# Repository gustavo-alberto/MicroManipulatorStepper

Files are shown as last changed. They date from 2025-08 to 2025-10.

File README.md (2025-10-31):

# Open Micro Manipulator

This project contains an open source low-cost, easy-to-build motorized **XYZ Micro-Manipulator** motion control platform achieving submicron precision.
It's designed for applications such as optical alignment, probing electronic components, and microscopy.

Check out the YouTube video for more information about the device and how it is built:<br>
[An Open Source Motorized XYZ Micro-Manipulator - Affordable sub µm Motion Control](https://youtu.be/MgQbPdiuUTw)

<div style="display: flex; gap: 2%;">
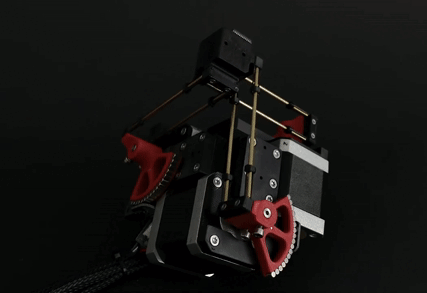
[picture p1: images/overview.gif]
  
  
</div>

Thanks to its parallel kinematic structure and miniature ball joints, it achieves good mechanical stiffness and a large range of motion.
The motors are off the shelf stepper motors driven by a 30 kHz closed loop controller and a very precise PWM signal.
A 'magnetic gearing' approach increases the resolution of the low-cost magnetic rotary encoders by a factor of 30 allowing for steps down to 50nm
(**Please mind the difference between resolution and accuracy**. The absolute accuracy is significantly worse.

The device can be controlled via simple G-Code commands over a USB serial interface and is thus easily integrated into other projects.
The firmware implements a complete motion planning stack with look-ahead for smooth and accurate path following capabilities.

## Getting Started

Below is a list of high level steps you can follow if you want to replicate the project. 
If you have questions or problems with the build or just want to discuss subjects related to the project, 
joint the projects community [Discord Server](https://discord.gg/maRvMVpa2Q).

1. Read this Document and watch the linked videos
2. Get the parts listed in [Bill of Materials](documentation/bom/bom.md)
3. Build the device and electronics
4. Change the hardware configuration according to your build [hw_config.h](firmware/MotionControllerRP/src/hw_config.h)
5. Upload firmware using VSCode with PlattformIO plugin
6. Calibrate axis

## 🐍 Python-API

The lightweight Python API handles all serial communication and provides convenient command execution and debug message printing.
The interface includes functions to home, move, and calibrate the device, as well as to query device information.
Simply copy the [open_micro_stage_api.py](software/PythonAPI/open_micro_stage_api.py) file into your project (also install the dependencies in requirements.txt), and you’re ready to get started.

## Usage Example
```python
from open_micro_stage_api import OpenMicroStageInterface

# create interface and connect
oms = OpenMicroStageInterface(show_communication=True, show_log_messages=True)
oms.connect('/dev/ttyACM0')

# run this once to calibrate joints
# for i in range(3): oms.calibrate_joint(i, save_result=True)

# home device
oms.home()

# move to several x,y,z positions [mm]
oms.move_to(0.0, 0.0, 0.0, f=10)
oms.move_to(3.1, 4.1, 5.9, f=26)
oms.move_to(0.0001, 0.0, 0.0, f=10)

# wait for moves to finish
oms.wait_for_stop()
```

## API Functions (most relevant functions only)
```python
connect(port, baud_rate=921600)
disconnect()
set_workspace_transform(transform)
get_workspace_transform()
home(axis_list=None)
calibrate_joint(joint_index, save_result)
move_to(x, y, z, f, move_immediately, blocking, timeout)
set_pose(x, y, z)
dwell(time_s, blocking, timeout)
enable_motors(enable)
wait_for_stop(polling_interval_ms, disable_callbacks)
set_max_acceleration(linear_accel, angular_accel)
set_servo_parameter(pos_kp, pos_ki, vel_kp, vel_ki, vel_filter_tc)
```

## ✨ Firmware v1.0.1

This update improves calibration, homing, logging, and adds several new G-Code commands.

### Improvements
- **Homing**: parallel homing support, higher repeatability, more accurate geometric reference  
- **Joint calibration**: refined procedure, persistent flash storage (no recalibration after reboot)  
- **Logging**: clearer and more detailed output  

### New G-Code Commands
- `G28` — Home joints (supports homing multiple axis simultanously for faster startup)
- `G24` — Set pose command (directly sets servo targets, bypassing motion controller)  
- `M17/M18` — Enable/Disable motors (with pose recovery from encoders on enable)  
- `M51` — Read encoder values  
- `M55` — Set servo loop parameters 
- `M56` — Joint calibration (with save-to-flash option)  
- `M57` — Read various information about the device state  
- `M58` — Read firmware version

## ⚙ CAD-Files

All CAD models are made in **FreeCAD** to allow everyone to view and modify the design without subscribing or paying for a proprietary CAD solution.
Note that most components are already designed with the goal to make them easily machinable on a 3-Axis CNC-Mill.
You can also 3D-Print the parts but have to live with thermal drift (carbon filled filaments can reduce this problem).

<div style="display: flex;">
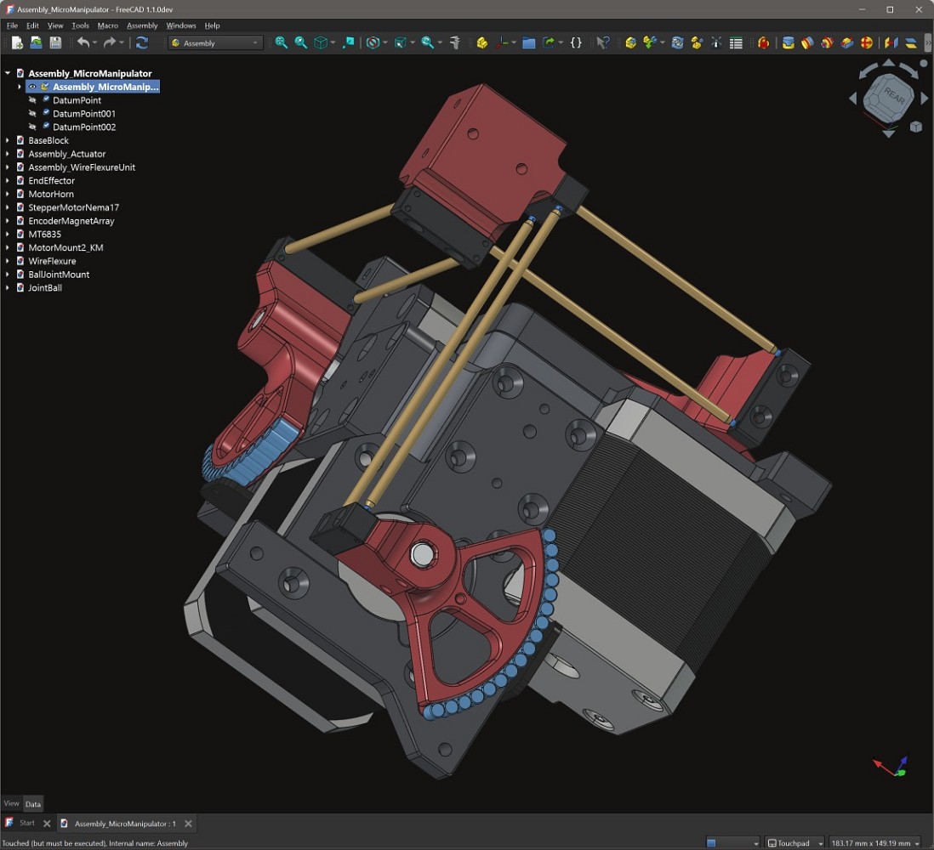
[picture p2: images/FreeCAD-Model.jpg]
FreeCAD Model
    
</div>

<br>

The CAD files can be found here: [CAD Models](construction).
Please note that FreeCAD version **1.1.0dev** was used, and the files might not work with older versions.

STL files for printing can be found here: [STL Files](construction/STL_3D_Printing/)

## ⚙ Kinematic Model

The kinematic model is defined here: [kinematic_model_delta3d.cpp](firmware/MotionControllerRP/src/kinemtaic_models/kinematic_model_delta3d.cpp).
Please check the dimensions of your build against the values set in the constructor. In particular, make sure the arm length matches.

## ⚙ Electronics

IMPORTANT: If you fabricated PCB version v1.2 (see version label on the board) you need to drill out a misplaced via on diode D1 that shorts 5V rail to ground (See [repair image](electronics/pcb_v1.2_fix.jpg) ). The problem was fixed in v1.3.

The electronics are designed in **KiCAD** and only commonly available modules (motor drivers and MCU boards) are used and connected by a simple PCB. No SMD soldering is required to populate the board to make the build extra accessible.
For usual winding resistance of your motors, the device should be powered by $${\color{lightgreen} 5V-6V }$$ (2A) to keep current and heating to a reasonable level.

<div style="display: flex; gap: 5%;">
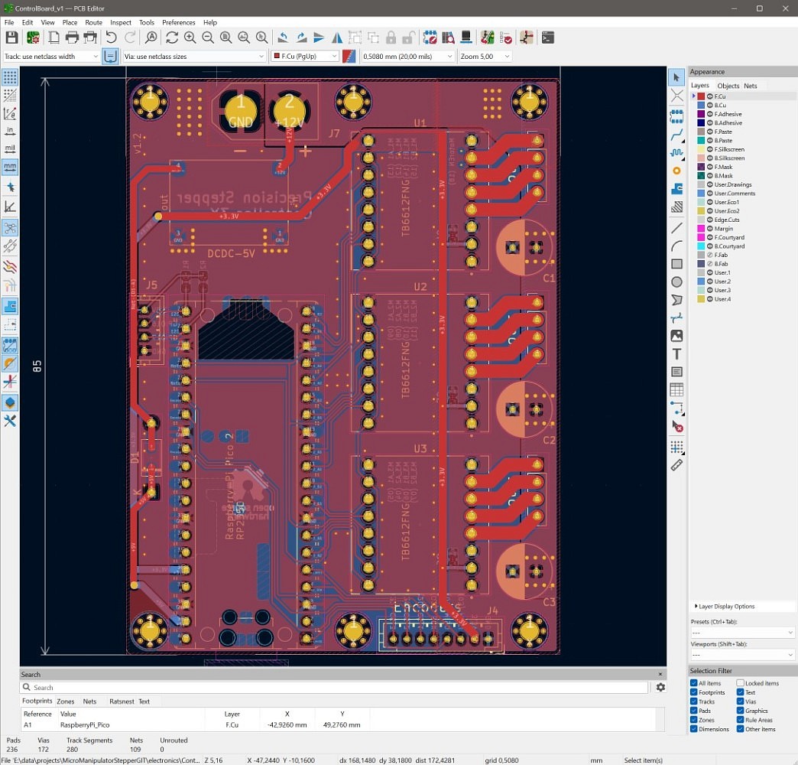
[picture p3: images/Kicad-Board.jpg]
  
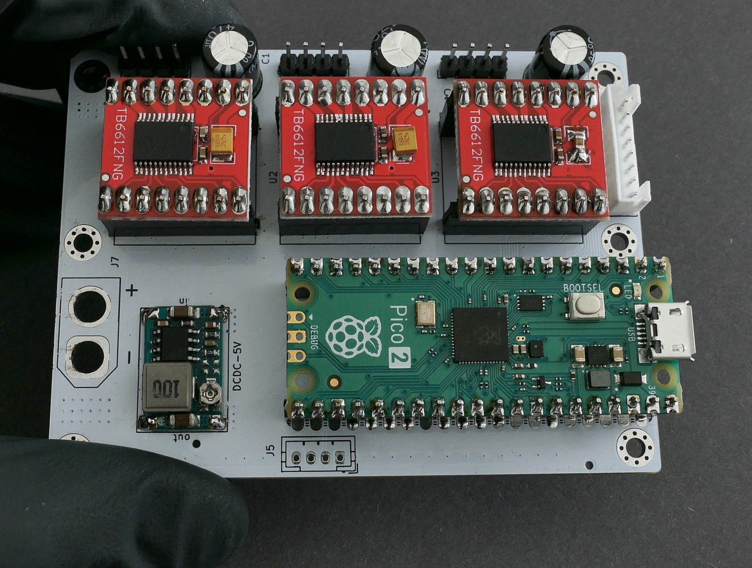
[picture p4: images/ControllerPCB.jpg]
  
</div>

## ⚙ Firmware

The firmware is written in C++ and takes some inspiration from the 'SimpleFOC' project. It aims to be streamlined and readable without any extra fuss, focusing on the hardware used in this project.
It implements path planning with look-ahead and, unlike many other motion controller projects, supports true 6DOF-Pose interpolation and planning, making it ready for driving hexapod motion platforms; that may or may not be the next step for this project.

You may find configuration for pin numbers, motor type, and other parameters in [hw_config.h](firmware/MotionControllerRP/src/hw_config.h). Please check them before uploading the firmware.

<div style="display: flex; gap: 2%;">
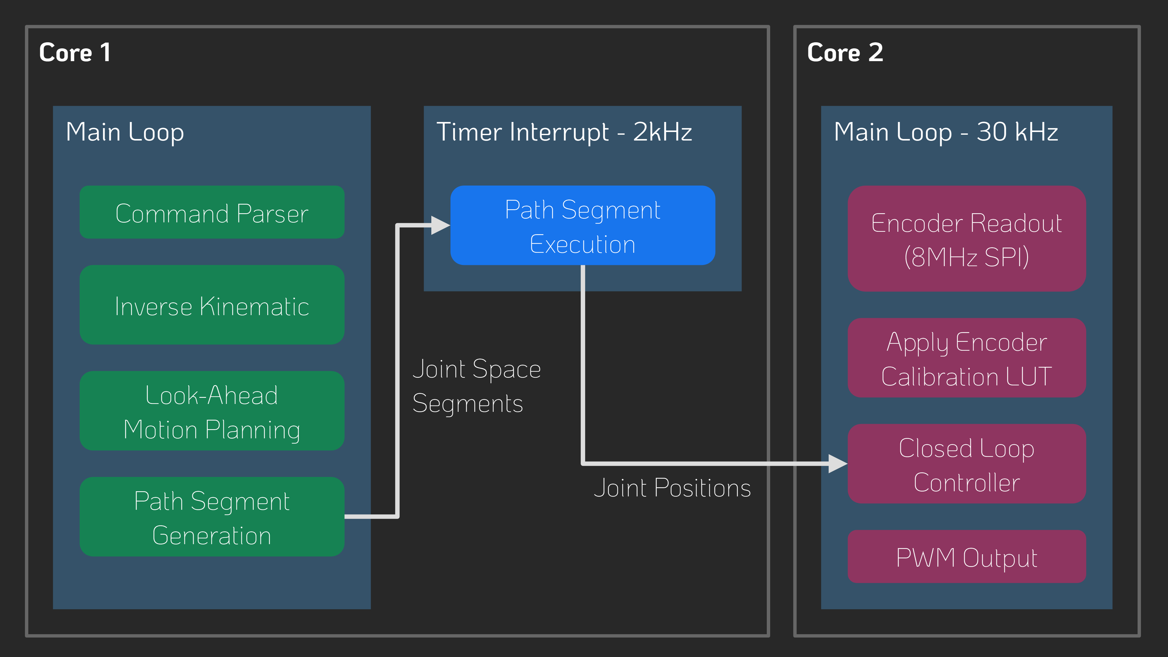
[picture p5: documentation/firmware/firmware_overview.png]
  
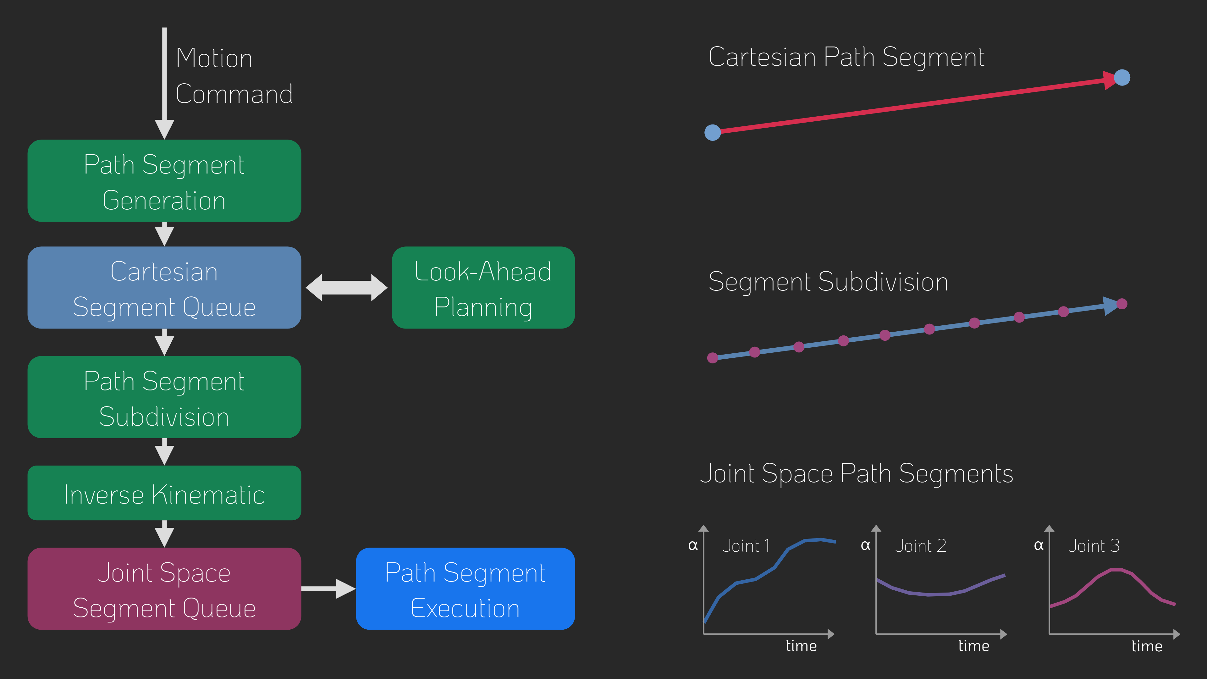
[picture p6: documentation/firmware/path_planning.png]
  
</div>

### Building and Flashing the Firmware

For building and flashing the firmware, Visual Studio Code (available for free on Windows and Linux) is recommended.
Install the PlatformIO add-on and open the firmware folder. You can now build and flash the firmware like any other PlatformIO project.

## ⚙ G-Code Interface

The firmware supports only a small subset of G-Code commands listed below.  
Each command is acknowledged with either an **`ok`** or **`error`** response.  

If a command provides additional information (e.g., the *get position* command), that information is returned **before** the `ok` message.  
The client must wait for an acknowledgment from the previous command before sending the next one—otherwise, behavior is undefined.
| Command           | Description                                                                 |
|-------------------|-----------------------------------------------------------------------------|
| `G0 X Y Z F`   | Move the end-effector in a straight line to the specified position. <br>• `X`, `Y`, `Z`: target positions <br>• `F`: feed rate |
| `G1 X Y Z F`   | Same as `G0`.                                                              |
| `G4 S/P`       | Dwell/pause for a specified time. <br>• `S`: seconds <br>• `P`: milliseconds |
| `G24 X Y Z A B C` | Directly set current pose for servo loops with optional rotation vector* `A`, `B`, `C`. |
| `G28 A-F`      | Home one or more joints. <br>• Optional joint selection `A`–`F`.           |
| `M17`          | Enable motors and read current pose as the start pose.                     |
| `M18`          | Disable motors.                                                            |
| `M50`          | Get current internal pose. (Encoders are not read here)                                   |
| `M51`          | Get current encoder angles (in degrees) and raw encoder values.              |
| `M52`          | Get the number of items in the planner queue.                               |
| `M53`          | Check if all planned moves are finished (`1` = finished, `0` = not finished). |
| `M55 A B C D F` | Set servo loop parameters. <br>• `A`, `B`: position PI controller gains (P and I) <br>• `C`, `D`: velocity PI controller gains (P and I) <br>• `F`: velocity filter time constant |
| `M56 J S`      | Calibrate a joint. <br>• `J`: joint index <br>• `S`: save calibration result |
| `M57`          | Get device and servo loop info: homing/calibration state, angles, loop frequencies, and file list. |
| `M58`          | Get firmware version.                                                      |
| `M204 L A`     | Set linear and angular acceleration. <br>• `L`: linear acceleration <br>• `A`: angular acceleration |

*Note: The communication protocol uses 3D vectors for rotations. The direction represents the rotation axis and the length of the vector represents the angle of rotation around the axis.

## ❤️ Support

If you'd like to support this project, consider the following:

- **Contribute to the build guide** – Help improve or expand the build instructions by submitting pull requests or opening issues with suggestions.
- **Characterize typical radial stepper motor shaft error motion** – Measure radial error motion of the shaft of multiple Nema-17 stepper motors (see Cylos Garage for more information about the subject: https://www.youtube.com/watch?v=gt2gK-oxy5s).
- **Give feedback on the build experience** – Let us know what worked, what didn’t, and how the process could be smoother for others.
- **Support the project on Ko-fi** – If you find this project valuable, you can support it financially via [Ko-fi](https://ko-fi.com/diffractionlimited) ☕.

## Youtube Video
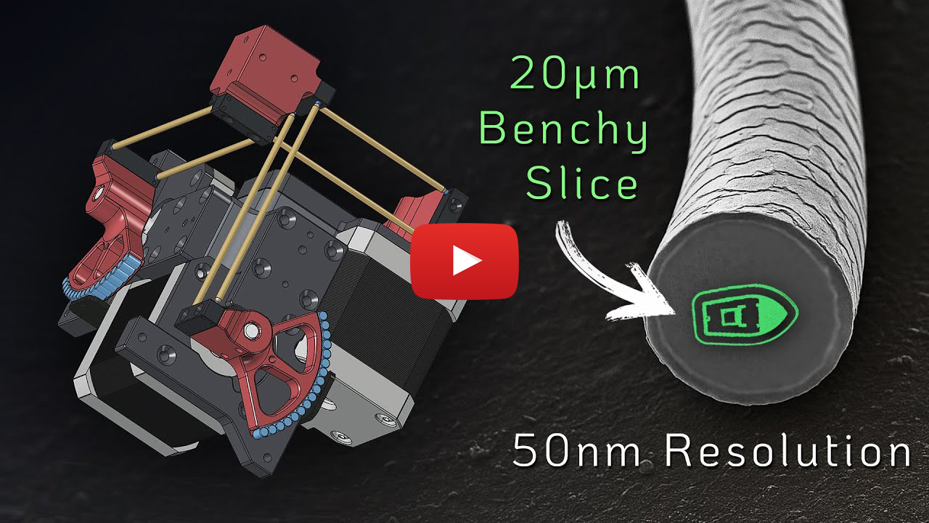
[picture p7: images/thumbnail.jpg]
Watch the video (https://youtu.be/MgQbPdiuUTw)


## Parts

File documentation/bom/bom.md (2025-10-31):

# Bill of Materials (BOM)

## Mechanics
| Name | Qty | Description | Comments | Suggested link | Image |
|------|-----|-------------|----------|----------------|-------|
| Steel ball | 12 | Ø1.25 mm (0.05") | Precision G10 or better. Can be sourced from small ball bearings | |
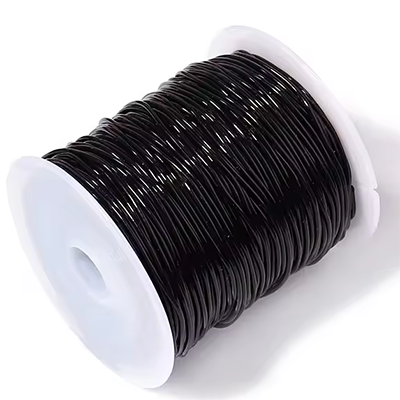
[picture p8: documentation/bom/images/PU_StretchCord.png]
Pu strech cord
| PU stretch cord | 1 m | Ø1mm | e.g. "Stretch Magic" or "Magic String" | [Aliexpress](https://www.aliexpress.us/item/3256805953910514.html)| |
| Neodym Cylinder Magnet | 70 | Ø3mm h=4 mm | N42 Grade | [Ebay Link](https://www.ebay.de/itm/365333642187?var=635110190027)|
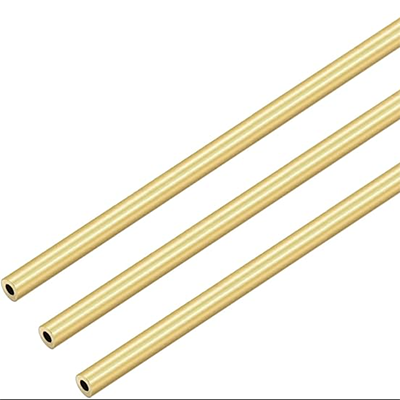
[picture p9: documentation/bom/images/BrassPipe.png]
Brass Pipe
| Brass Pipe | 1 m | OD=Ø2mm ID=Ø1 mm |  | [Amazon](https://a.co/d/1pRFmtf)| |
| M2 Screw | 12 | M2×12 mm, Countersunk |  | |
| M3 Grub Screw | 6 | M3×4 |  | |

## Electronics
| Name | Qty | Description | Comments | Suggested link | Image |
|------|-----|-------------|----------|----------------|-------|
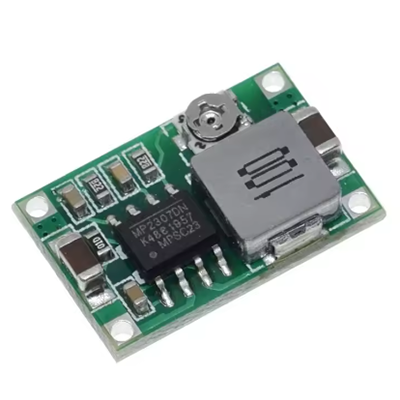
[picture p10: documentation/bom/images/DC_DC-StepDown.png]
DC-DC Step Down
| DC-DC Step Down Module | 1 | 4.75–23 V Step-Down Buck Converter |  | [Aliexpress](https://www.aliexpress.us/item/3256806752772875.html)| |
| (1N5819) OR (PMEG4010) | 1 | Diode (through-hole or SMD) |  | |
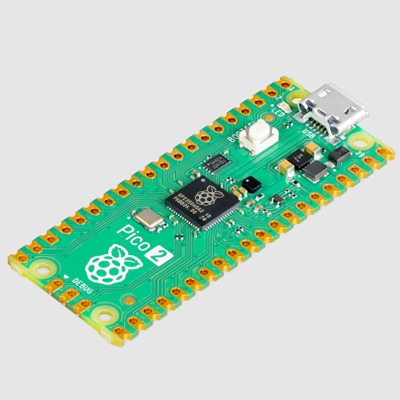
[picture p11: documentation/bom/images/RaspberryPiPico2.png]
Raspberry Pi Pico 2
| Raspberry Pi Pico 2 | 1 | Microcontroller board |  | | |
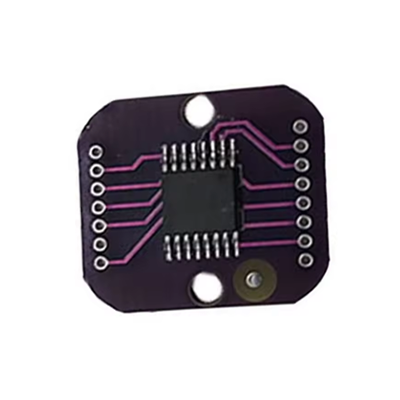
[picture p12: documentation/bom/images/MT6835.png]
MT6835 Magnetic Encoder Module
| MT6835 Magnetic Encoder Module | 3 | Magnetic encoder |  | [Aliexpress](https://www.aliexpress.us/item/3256808005140674.html)| |
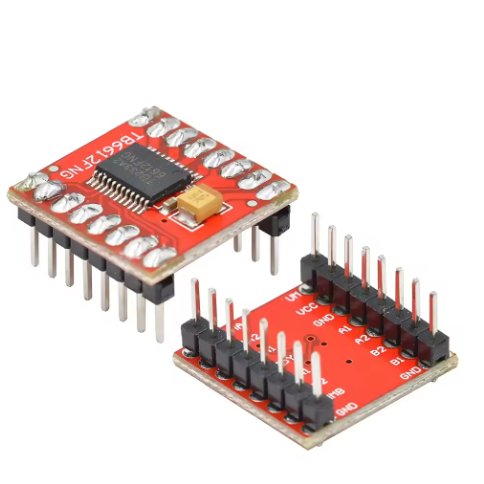
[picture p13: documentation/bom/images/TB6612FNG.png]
TB6612FNG Driver
| TB6612FNG Driver | 3 | |  | [Aliexpress](https://www.aliexpress.us/item/3256806060073976.html)| |
| 470 µF Electrolytic Capacitor | 3 | > 100 µF | anything > 100µF will work well | |
| 10 µF Ceramic Capacitor 0603 | 3 | Optional |  | |
| 4.7 k Resistor 0603 | 2 | Optional |  | |
| 2 Pin Power Header | 1 | 7.5 mm pitch |  | |
| 4 Pin Header | 4 | 2.5 mm pitch |  | |
| 8 Pin Header | 1 | 2.0 mm pitch |  | |
| NEMA 17 Stepper Motor | 3 | Body ≤ 38 mm | Body length <= 38mm | |

## 3D Printing
| Name | Qty | Description | Comments | Image |
|------|-----|-------------|----------|-------|
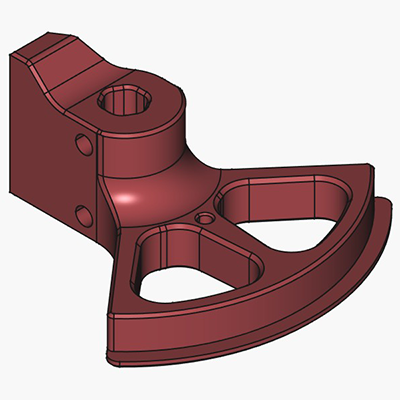
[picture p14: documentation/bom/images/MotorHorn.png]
Motor Horn
| Motor Horn | 3 |  | 0.4 mm+ nozzle may require post-processing | |
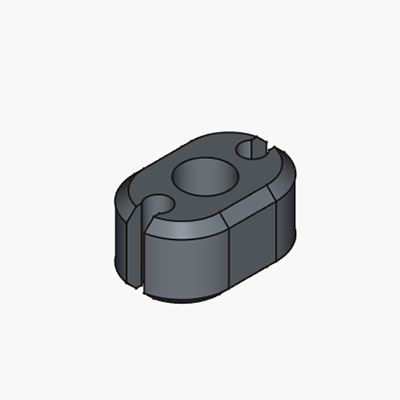
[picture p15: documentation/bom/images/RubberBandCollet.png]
Rubber Band Collet
| RubberBandCollet | 12 |  | 0.4 mm nozzle, 0.1mm Layer height + may require post-processing | |
| BallJointMount | 6 |  | 0.4 mm nozzle, 0.1mm Layer height + may require post-processing | Ball Joint Mount|
| Motor Mount | 3 |  |  | Motor Mount|
| End Effector | 1 |  |  | End Effector|
| Base Block | 1 |  |  | Base Block|

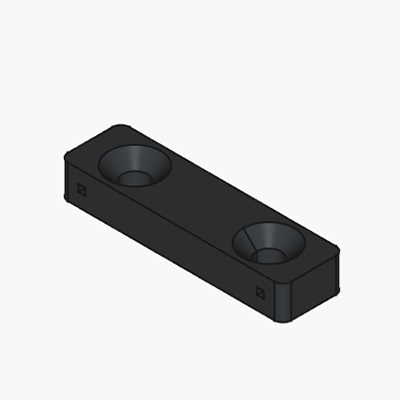
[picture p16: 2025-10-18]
documentation/bom/images/WireFlexureMount.png

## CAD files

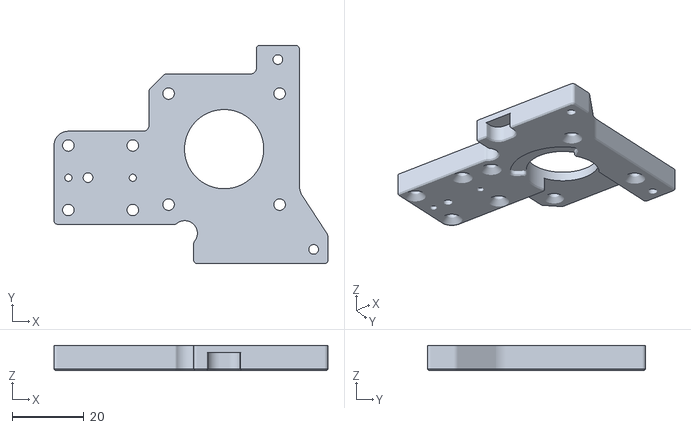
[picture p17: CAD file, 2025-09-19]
construction/v3_3dprinting_stl/MotorMount.stl
76.5 x 61.0 x 7.00

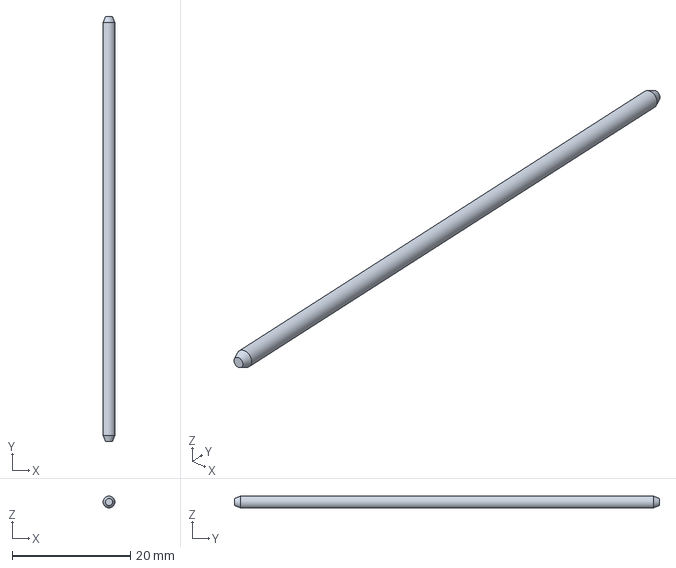
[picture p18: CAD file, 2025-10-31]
construction/v3/WireFlexure.FCStd
2.00 x 72.0 x 2.00 mm

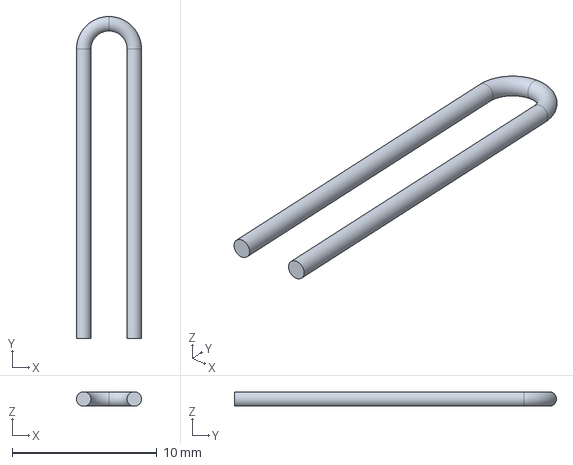
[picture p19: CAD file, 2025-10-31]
construction/v3/RubberBand.FCStd
4.50 x 22.2 x 1 mm

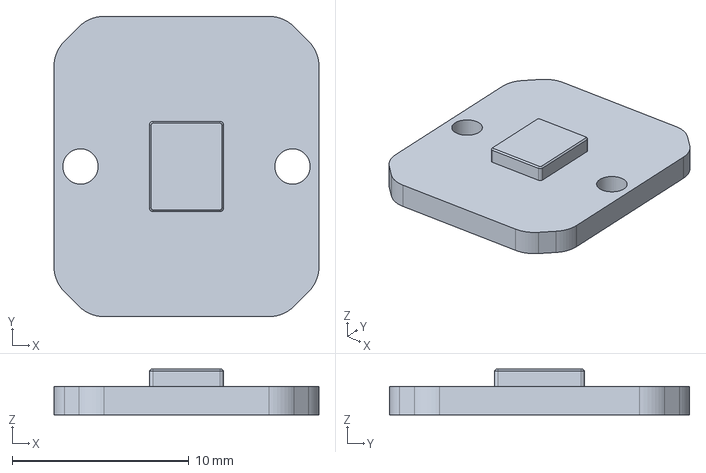
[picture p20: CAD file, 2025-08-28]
construction/v3/MT6835.FCStd
15.0 x 17.0 x 2.60 mm

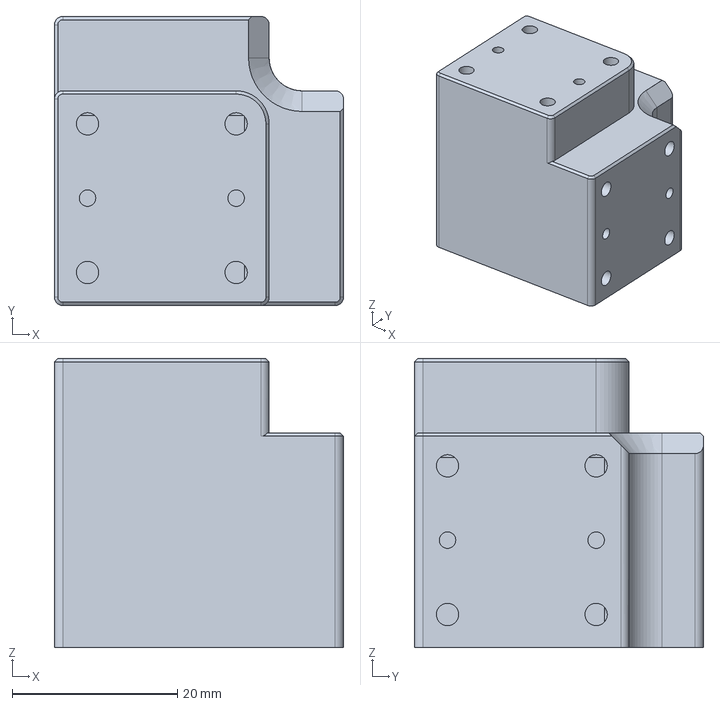
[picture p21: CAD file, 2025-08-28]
construction/v3/BaseBlock.FCStd
35.0 x 35.0 x 35.0 mm

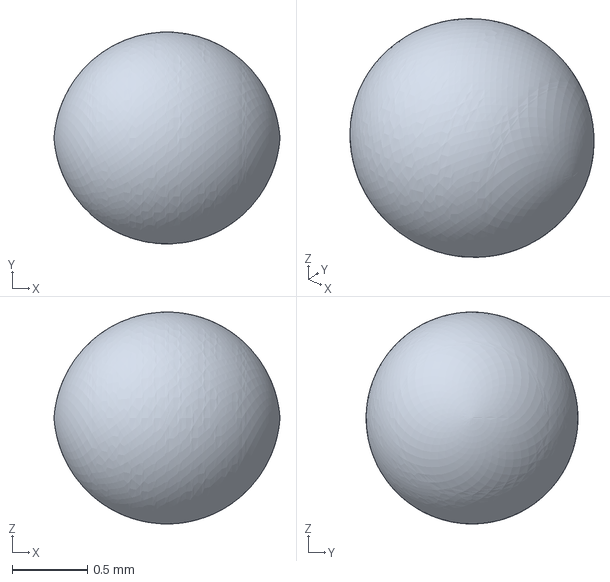
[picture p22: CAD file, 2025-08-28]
construction/v3/JointBall.FCStd
1.50 x 1.40 x 1.40 mm

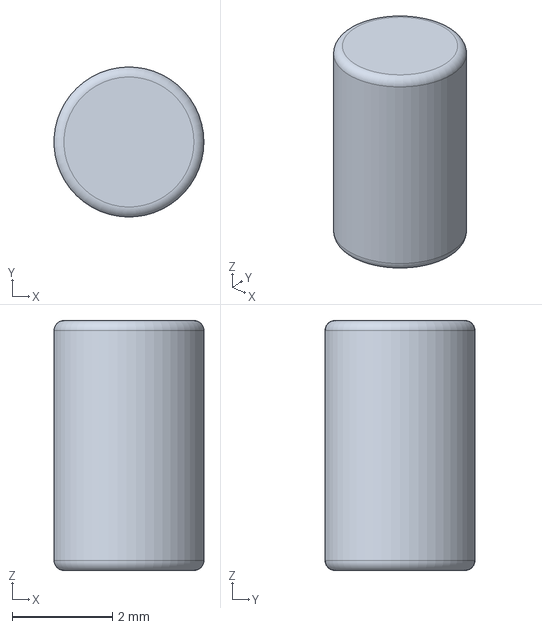
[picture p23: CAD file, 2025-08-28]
construction/v3/EncoderMagnet.FCStd
3.00 x 3.00 x 5.00 mm

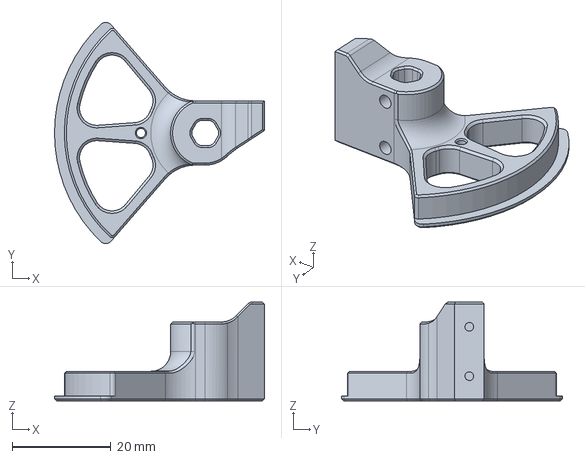
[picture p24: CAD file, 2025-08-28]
construction/v3/MotorHorn.FCStd
42.5 x 44.7 x 20.0 mm

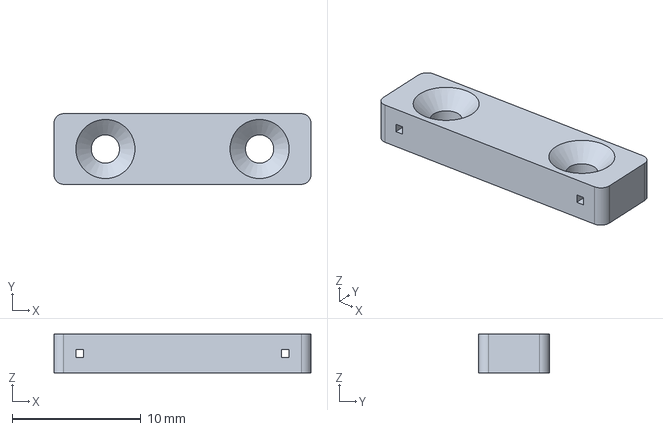
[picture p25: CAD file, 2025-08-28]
construction/v3/WireFlexureMount.FCStd
20.0 x 5.50 x 3.00 mm

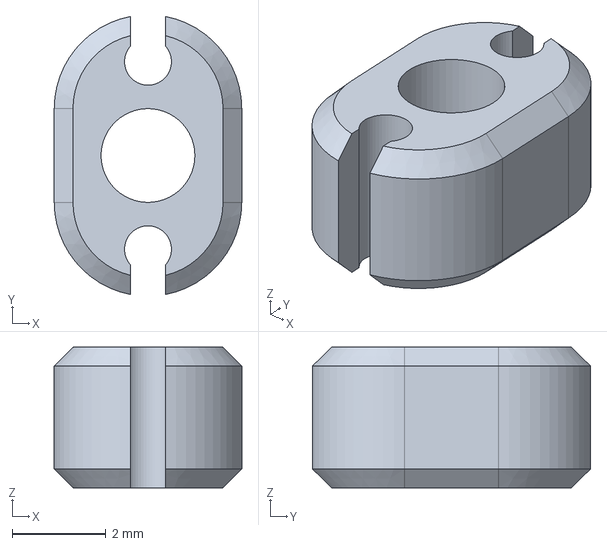
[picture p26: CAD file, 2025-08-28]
construction/v3/RubberBandCollet.FCStd
4.00 x 5.93 x 3.00 mm

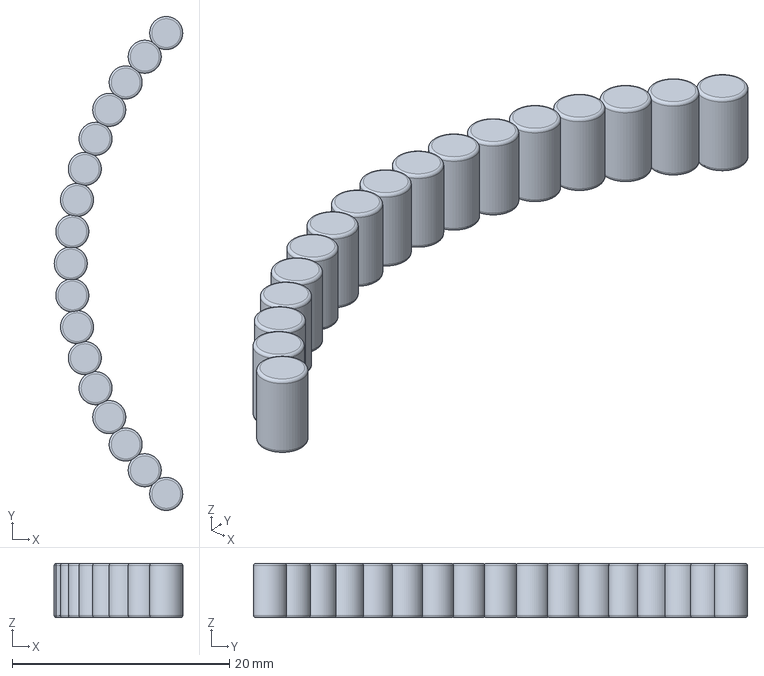
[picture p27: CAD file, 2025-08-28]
construction/v3/EncoderMagnetArray.FCStd
11.8 x 45.5 x 5.00 mm

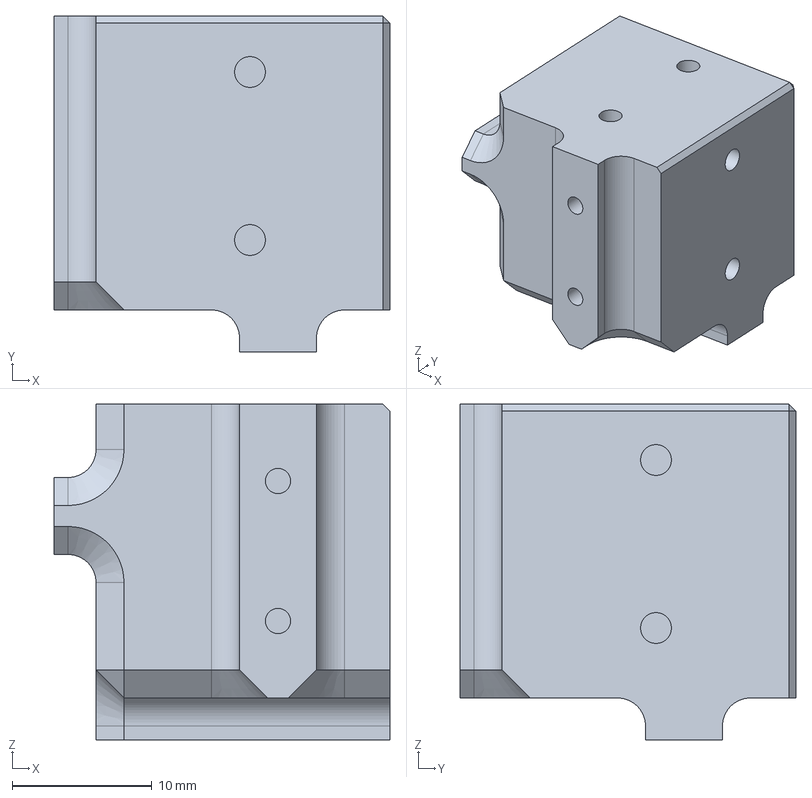
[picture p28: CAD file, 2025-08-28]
construction/v3/EndEffector.FCStd
24.0 x 24.0 x 24.0 mm

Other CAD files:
construction/v3/Assembly_MicroManipulator.FCStd
construction/v3/Assembly_Actuator.FCStd
construction/v3/Assembly_WireFlexureUnit.FCStd
construction/v3/Assembly_MicroManipulator_backup.FCStd
construction/v3/Assembly_EndEffector.FCStd
construction/v3/MotorMount2_KM.FCStd
construction/v3/BallJointMount.FCStd
construction/v3/StepperMotorNema17.FCStd
construction/v3_3dprinting_stl/BallJointMount.stl
construction/v3_3dprinting_stl/BaseBlock.stl
construction/v3_3dprinting_stl/EndEffector.stl
construction/v3_3dprinting_stl/MotorHorn.stl
construction/v3_3dprinting_stl/RubberBandCollet.stl
construction/v3_3dprinting_stl/WireFlexureMount.stl

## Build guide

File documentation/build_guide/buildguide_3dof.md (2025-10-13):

# Open MircoManipulator 3DOF - Build Guide

This document shall provide an easy to follow build guide and help with material selection like glues/magnets and so on.
The following structure is just a placeholder, feel free to contribute...

## Introduction

## Bill of Materials

## Components
### Mechanical Parts
### Magnet Selection

## Balljoints
## Assembly

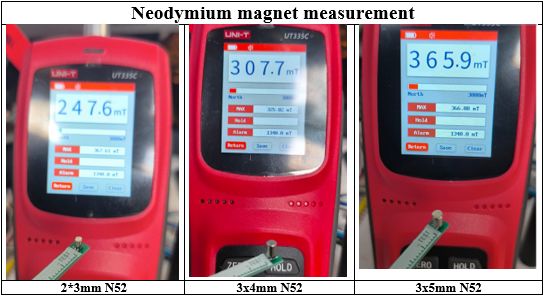
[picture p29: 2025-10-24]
documentation/build_guide/images/MagnetFieldStrengthComparison.jpg

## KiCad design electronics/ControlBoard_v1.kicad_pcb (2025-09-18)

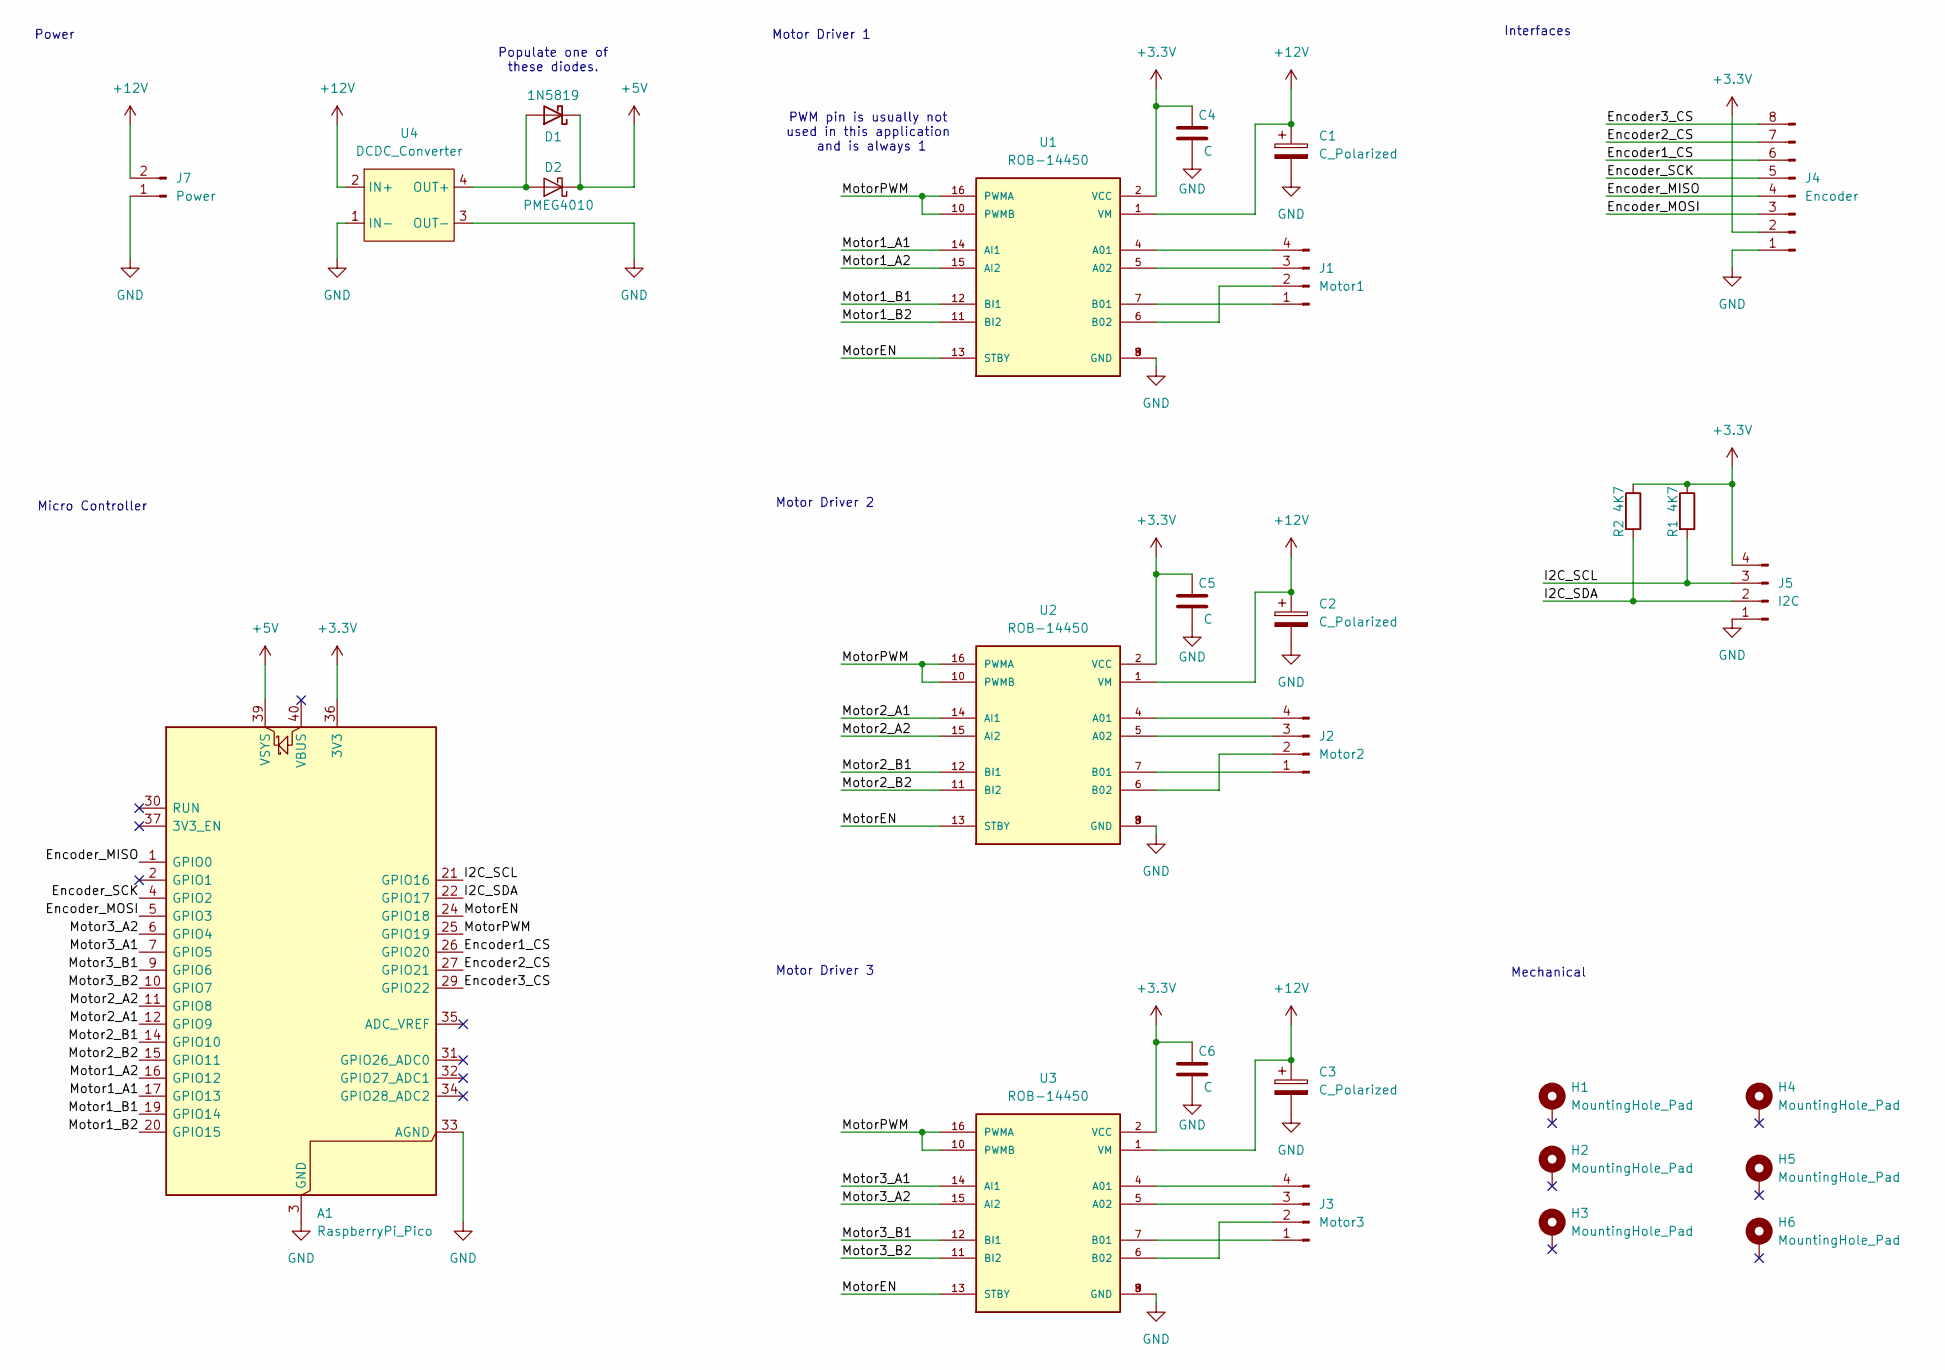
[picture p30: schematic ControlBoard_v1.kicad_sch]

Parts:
A1: RaspberryPi_Pico; RaspberryPi_Pico_Common_Unspecified
C1, C2, C3: C_Polarized; CP_Radial_D8.0mm_P3.50mm
C4, C5, C6: C; C_0603_1608Metric_Pad1.08x0.95mm_HandSolder
D1: 1N5819; D_DO-41_SOD81_P10.16mm_Horizontal
D2: PMEG4010; D_SOD-123F
H1, H2, H3, H4, H5, H6: MountingHole_Pad; MountingHole_2.7mm_M2.5_Pad_Via
J1: Motor1; PinHeader_1x04_P2.54mm_Vertical
J2: Motor2; PinHeader_1x04_P2.54mm_Vertical
J3: Motor3; PinHeader_1x04_P2.54mm_Vertical
J4: Encoder; JST_PH_B8B-PH-K_1x08_P2.00mm_Vertical
J5: I2C; JST_PH_B4B-PH-K_1x04_P2.00mm_Vertical
J7: Power; AMASS_XT60-M_1x02_P7.20mm_Vertical
R1, R2: 4K7; R_0603_1608Metric_Pad0.98x0.95mm_HandSolder
U1, U2, U3: ROB-14450; MODULE_ROB-14450; PARTREV 11-13-17
U4: DCDC_Converter; DCDC_17mmx12mm

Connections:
+3.3V: A1.36 (3V3), C4.1, C5.1, C6.1, J4.2, J5.4, R1.1, R2.1, U1.2 (VCC), U2.2 (VCC), U3.2 (VCC)
+5V: A1.39 (VSYS), D1.1 (K), D2.1 (K)
+12V: C1.1, C2.1, C3.1, J7.2, U1.1 (VM), U2.1 (VM), U3.1 (VM), U4.2 (IN+)
/Encoder1_CS: A1.26 (GPIO20), J4.6
/Encoder2_CS: A1.27 (GPIO21), J4.7
/Encoder3_CS: A1.29 (GPIO22), J4.8
/Encoder_MISO: A1.1 (GPIO0), J4.4
/Encoder_MOSI: A1.5 (GPIO3), J4.3
/Encoder_SCK: A1.4 (GPIO2), J4.5
/I2C_SCL: A1.21 (GPIO16), J5.3, R1.2
/I2C_SDA: A1.22 (GPIO17), J5.2, R2.2
/Motor1_A1: A1.17 (GPIO13), U1.14 (AI1)
/Motor1_A2: A1.16 (GPIO12), U1.15 (AI2)
/Motor1_B1: A1.19 (GPIO14), U1.12 (BI1)
/Motor1_B2: A1.20 (GPIO15), U1.11 (BI2)
/Motor2_A1: A1.12 (GPIO9), U2.14 (AI1)
/Motor2_A2: A1.11 (GPIO8), U2.15 (AI2)
/Motor2_B1: A1.14 (GPIO10), U2.12 (BI1)
/Motor2_B2: A1.15 (GPIO11), U2.11 (BI2)
/Motor3_A1: A1.7 (GPIO5), U3.14 (AI1)
/Motor3_A2: A1.6 (GPIO4), U3.15 (AI2)
/Motor3_B1: A1.9 (GPIO6), U3.12 (BI1)
/Motor3_B2: A1.10 (GPIO7), U3.11 (BI2)
/MotorEN: A1.24 (GPIO18), U1.13 (STBY), U2.13 (STBY), U3.13 (STBY)
/MotorPWM: A1.25 (GPIO19), U1.10 (PWMB), U1.16 (PWMA), U2.10 (PWMB), U2.16 (PWMA), U3.10 (PWMB), U3.16 (PWMA)
GND: A1.3 (GND), A1.8 (GND), A1.13 (GND), A1.18 (GND), A1.23 (GND), A1.28 (GND), A1.33 (AGND), A1.38 (GND), C1.2, C2.2, C3.2, C4.2, C5.2, C6.2, J4.1, J5.1, J7.1, U1.3 (GND), U1.8 (GND), U1.9 (GND), U2.3 (GND), U2.8 (GND), U2.9 (GND), U3.3 (GND), U3.8 (GND), U3.9 (GND), U4.1 (IN-), U4.3 (OUT-)
unnamed: D1.2 (A), D2.2 (A), U4.4 (OUT+)
unnamed: J1.1, U1.7 (B01)
unnamed: J1.2, U1.6 (B02)
unnamed: J1.3, U1.5 (A02)
unnamed: J1.4, U1.4 (A01)
unnamed: J2.1, U2.7 (B01)
unnamed: J2.2, U2.6 (B02)
unnamed: J2.3, U2.5 (A02)
unnamed: J2.4, U2.4 (A01)
unnamed: J3.1, U3.7 (B01)
unnamed: J3.2, U3.6 (B02)
unnamed: J3.3, U3.5 (A02)
unnamed: J3.4, U3.4 (A01)

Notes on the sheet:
PWM pin is usually not used in this application and is always 1
Motor Driver 2
Power
Interfaces
Motor Driver 1
Motor Driver 3
Mechanical
Populate one of these diodes.
Micro Controller

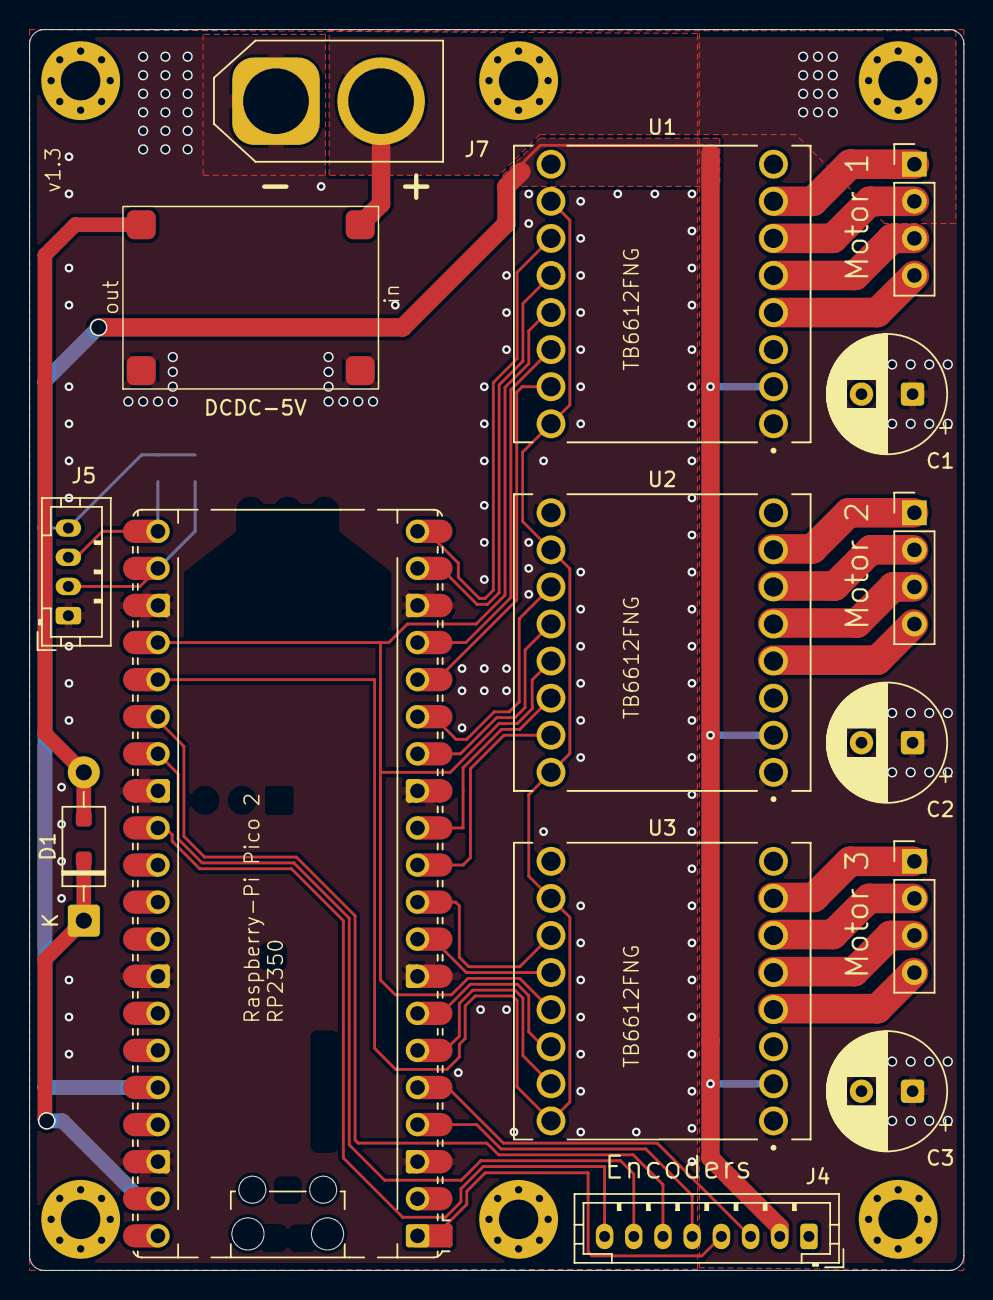
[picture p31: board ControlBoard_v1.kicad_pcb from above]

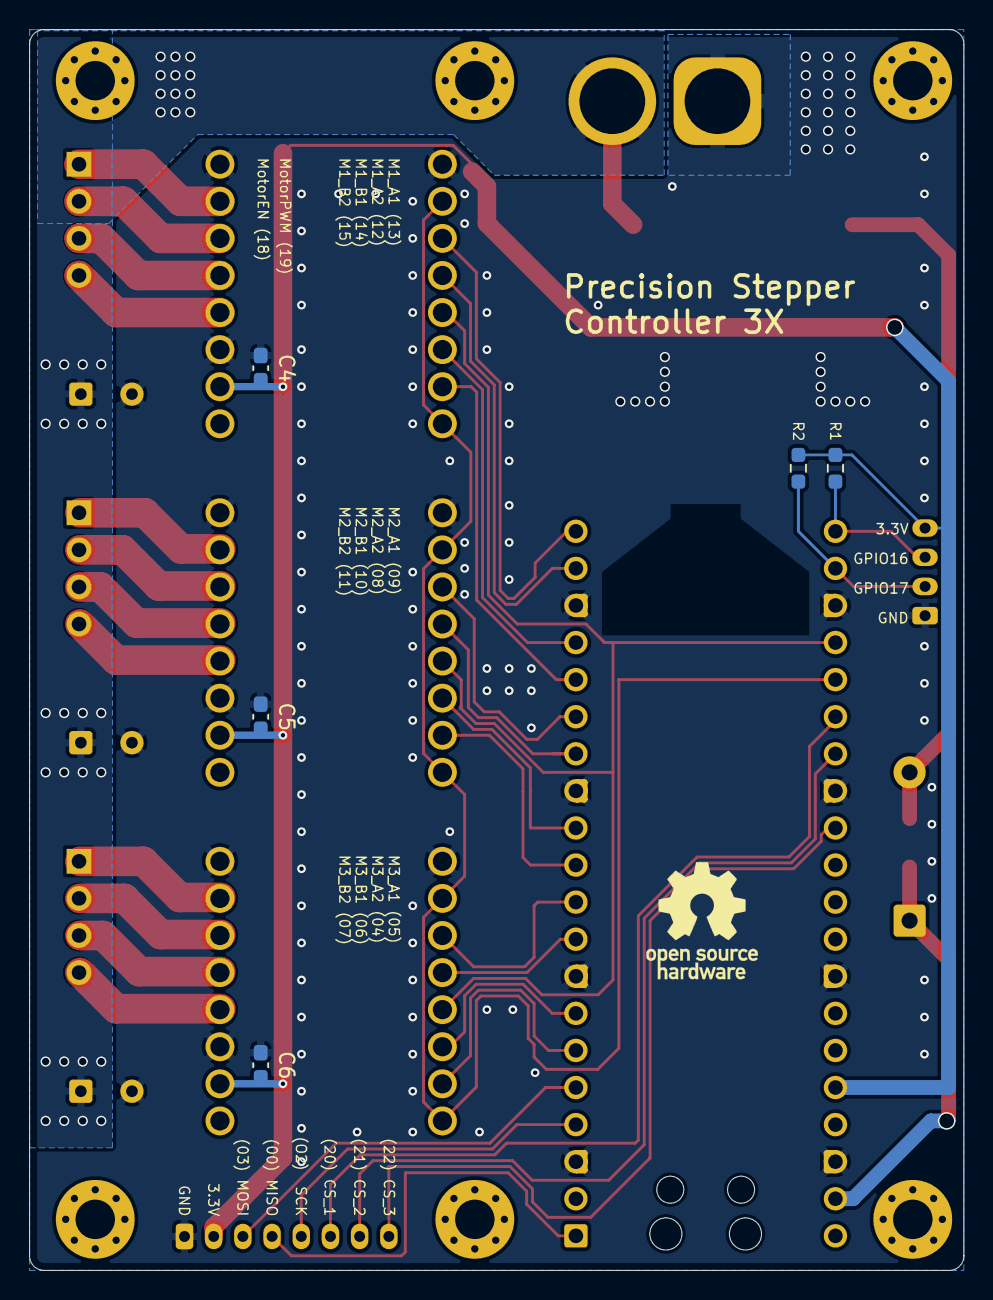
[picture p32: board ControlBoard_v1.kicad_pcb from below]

Board: 2 copper layers, 64.0 x 85.0 mm, 27 parts (6 on the bottom side), 39 nets.

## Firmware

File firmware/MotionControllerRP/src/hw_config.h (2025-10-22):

#pragma once
#include "utilities/math_constants.h"

//--- MOTORS ------------------------------------------------------------------

// motor pole pair count
//  * 100 for 0.9deg stepper motors
//  * 50  for 1.8deg stepper motors
constexpr float MOTOR1_POLE_PAIRS = 100;
constexpr float MOTOR2_POLE_PAIRS = 100;
constexpr float MOTOR3_POLE_PAIRS = 100;

//--- ENCODERS ----------------------------------------------------------------

// Conversion factor from encoder angle (one 2pi period every two magnets) to rotor angle.
// Used when the system can not rely on calibration data being present (e.g. during homing)
constexpr float ENCODER_MAGNET_PITCH = 3.0f;    // [mm]
constexpr float ENCODER_MAGNET_RADIUS = 30.0f;  // [mm]
constexpr float ENCODER_ANGLE_TO_ROTOR_ANGLE = (ENCODER_MAGNET_PITCH*2.0f) / 
                                               (ENCODER_MAGNET_RADIUS * Constants::TWO_PI_F);

//--- HOMING ------------------------------------------------------------------

constexpr float HOMING_VELOCITY   = 1.0f;        // rad per s
constexpr float HOMING_CURRENT    = 0.15f;       // range 0..1
constexpr float HOMING_FINISH_POS = 0.5f;        // in rad

//--- CALIBRATION -------------------------------------------------------------

// degrees from home position
constexpr float CALIBRATION_RANGE = 95; 

// velocity of the magnetic field during calibration (lower is more accurate)
constexpr float CALIBRATION_FIELD_VELOCITY = 40.0f; 

//--- PINS --------------------------------------------------------------------

// #define SINGLE_AXIS_BOARD
#ifndef SINGLE_AXIS_BOARD
  // Pins for 3Axis Board
  #define PIN_BUILTIN_LED 23
  #define PIN_USER_BUTTON 24

  #define PIN_M1_PWM_A_POS  13
  #define PIN_M1_PWM_A_NEG  12
  #define PIN_M1_PWM_B_POS  14
  #define PIN_M1_PWM_B_NEG  15

  #define PIN_M2_PWM_A_POS  9
  #define PIN_M2_PWM_A_NEG  8
  #define PIN_M2_PWM_B_POS  10
  #define PIN_M2_PWM_B_NEG  11

  #define PIN_M3_PWM_A_POS  5
  #define PIN_M3_PWM_A_NEG  4
  #define PIN_M3_PWM_B_POS  6
  #define PIN_M3_PWM_B_NEG  7


  #define PIN_MOTOR_EN      18
  #define PIN_MOTOR_PWMAB   19

  #define PIN_ENCODER1_CS 20
  #define PIN_ENCODER2_CS 21
  #define PIN_ENCODER3_CS 22
  #define PIN_ENCODER_SCK 2
  #define PIN_ENCODER_MISO 0
  #define PIN_ENCODER_MOSI 3

#else
  // Single Axis Board
  #define PIN_BUILTIN_LED 16
  #define PIN_USER_BUTTON 24

  #define PIN_M1_PWM_A_POS  13
  #define PIN_M1_PWM_A_NEG  12
  #define PIN_M1_PWM_B_POS  14
  #define PIN_M1_PWM_B_NEG  15

  #define PIN_M2_PWM_A_POS  9
  #define PIN_M2_PWM_A_NEG  8
  #define PIN_M2_PWM_B_POS  10
  #define PIN_M2_PWM_B_NEG  11

  #define PIN_M3_PWM_A_POS  5
  #define PIN_M3_PWM_A_NEG  4
  #define PIN_M3_PWM_B_POS  6
  #define PIN_M3_PWM_B_NEG  7


  #define PIN_MOTOR_EN      18
  #define PIN_MOTOR_PWMAB   19

  #define PIN_ENCODER1_CS 20
  #define PIN_ENCODER2_CS 21
  #define PIN_ENCODER3_CS 22
  #define PIN_ENCODER_SCK 2
  #define PIN_ENCODER_MISO 0
  #define PIN_ENCODER_MOSI 3
#endif

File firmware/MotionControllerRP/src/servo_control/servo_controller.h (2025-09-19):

// --------------------------------------------------------------------------------------
// Project: MicroManipulatorStepper
// License: MIT (see LICENSE file for full description)
//          All text in here must be included in any redistribution.
// Author:  M. S. (diffraction limited)
// --------------------------------------------------------------------------------------

#pragma once

#include "hardware/MT6835_encoder.h"
#include "hardware/TB6612_motor_driver.h"
#include "utilities/lookup_table.h"
#include "pid.h"

//*** CLASS *****************************************************************************

class ServoController {
  public:
    // use defines instead of virtual functions for speed
    // TODO: check if this makes any difference and change accordingly
    typedef TB6612MotorDriver MOTOR_DRIVER_TYPE;
    typedef MT6835Encoder ENCODER_TYPE;

  public:
    ServoController(MOTOR_DRIVER_TYPE& motor_driver, ENCODER_TYPE& encoder, int32_t motor_pole_pairs);

    // initialize the servo controller hardware
    void init(float max_motor_amplitude);

    // set the encoder raw angle to motor position lookup table
    void set_enc_to_pos_lut(LookupTable& lut);
    // get the encoder raw angle to motor position lookup table
    const LookupTable& get_enc_to_pos_lut() const;

    // set the motor position to field angle lookup table
    void set_pos_to_field_lut(LookupTable& lut);
    // get the motor position to field angle lookup table
    const LookupTable& get_pos_to_field_lut() const;

    // Updates the servo loop. 
    void update(float target_motor_pos,
                float dt,
                float one_over_dt);

    // Checks if the motor is at position (uses values from previous update() call).
    bool at_position(float motor_pos_eps);

    // Reads the current motor position from the encoder.
    float read_position();

    // Returns the motor position.
    float get_position();

    // Returns the current position error from the last servo loop update.
    float get_position_error();

    // Moves to a new motor position using closed loop control (blocking).
    bool move_to(float target_motor_angle, 
                 float at_pos_motor_angle_eps, 
                 float settle_time_ms,
                 float timeout_us);

    // Moves to a new motor position using open loop controll (blocking).
    // Motor updates must be disabled if servo loop is running in background.
    void move_to_open_loop(float target_motor_angle, 
                           float angular_velocity);
    
    // Returns the encoder object.
    ENCODER_TYPE& get_encoder();

    // Returns the motor driver object.
    MOTOR_DRIVER_TYPE& get_motor_driver();

    // Returns number of motor pole pairs.
    // Can be used to approximate conversion of motor position to field angle.
    float get_pole_pair_count();

    // enable or disable motor 
    void set_motor_enabled(bool enable, bool synchronize_field_angle);

    // enable or disable motor updates
    void set_motor_update_enabled(bool enable);

    // enable or disable encoder reads
    void set_encoder_update_enabled(bool enable);

  public:
    float encoder_angle_to_motor_pos(int32_t encoder_angle_raw);
    float motor_pos_to_field_angle(float motor_pos);
    float motor_pos_to_field_angle_derivative(float motor_pos);

  public:
    LowpassFilter velocity_lowpass;
    PIDController pos_controller;
    PIDController velocity_controller;

  private:
    ENCODER_TYPE& encoder;
    MOTOR_DRIVER_TYPE& motor_driver;
    LookupTable encoder_raw_to_motor_pos_lut;
    LookupTable motor_pos_to_field_angle_lut;

    float motor_pole_pair_count = 0.0f;   // number as motor pole pairs (as float to avoid repeated conversion)
    float motor_current_amplitude = 0.5f; // motor current in range [0..1]
    float motor_pos = 0;                  // current motor position
    float motor_pos_prev = 0;             // previous motor position
    float pos_error = 0;                  // current position error as computed by upate()
    float velocity = 0;                   // current velocity estimate
    float output = 0.0f;                  // servo loop output (field angle offset)
    bool motor_update_enabled = false;    // enables mootor field updates
    bool encoder_update_enabled = true;   // enables encoder reads
};

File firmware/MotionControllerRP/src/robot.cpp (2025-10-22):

// --------------------------------------------------------------------------------------
// Project: MicroManipulatorStepper
// License: MIT (see LICENSE file for full description)
//          All text in here must be included in any redistribution.
// Author:  M. S. (diffraction limited)
// --------------------------------------------------------------------------------------

#include <LittleFS.h> 
#include "robot.h"
#include "hw_config.h"
#include "utilities/logging.h"
#include "utilities/utilities.h"
#include "kinematic_models/kinematic_model_delta3d.h"
#include "servo_control/homing_controller.h"
#include "servo_control/actuator_calibration.h"
#include "pico/multicore.h"
#include "version.h"

constexpr int SPINLOCK_ID_SHARED_DATA = 0;
constexpr int SPINLOCK_ID_JOINTS = 1;

//*** FUNCTION **************************************************************************

bool startswith(const std::string& str, const std::string& prefix) {
    return str.size() >= prefix.size() &&
           std::equal(prefix.begin(), prefix.end(), str.begin());
}

//*** CLASS *****************************************************************************

//--- RobotAxis -------------------------------------------------------------------------

RobotJoint::RobotJoint(MT6835Encoder* encoder, 
                       TB6612MotorDriver* motor_driver,
                       int pole_pairs) 
{
  RobotJoint::encoder = encoder;
  RobotJoint::motor_driver = motor_driver;
  servo_controller = new ServoController(*motor_driver, *encoder, pole_pairs);
  position = 0.0f;
  velocity = 0.0f;
}

RobotJoint::~RobotJoint() {
  delete servo_controller;
  delete motor_driver;
  delete encoder;
  servo_controller = nullptr;
  motor_driver = nullptr;
  encoder = nullptr;
}

void RobotJoint::init(int joint_idx) {
  RobotJoint::joint_idx = joint_idx;

  encoder->init(0x5, 0x4);
  servo_controller->init(0.5);
  servo_controller->set_motor_enabled(false, false);
}

bool RobotJoint::calibrate(bool print_measurements) {
  LOG_INFO("Joint-%i: calibrating joint...", joint_idx);

  HomingController homing_controller;
  bool homing_ok = homing_controller.run_blocking(servo_controller, -HOMING_VELOCITY, 
                                                  360.0f*DEG_TO_RAD, HOMING_CURRENT,
                                                  ENCODER_ANGLE_TO_ROTOR_ANGLE);
  if(homing_ok == false) {
    LOG_ERROR("Joint-%i: Calibration failed due to unsuccessful homing sequence", joint_idx);
    return false;
  }

  // measure lookup tables
  LookupTable encoder_raw_to_motor_pos_lut;
  LookupTable motor_pos_to_field_angle_lut;
  bool ok = measure_calibration_data(encoder_raw_to_motor_pos_lut, 
                                     motor_pos_to_field_angle_lut, 
                                     *servo_controller, 
                                     CALIBRATION_RANGE*DEG_TO_RAD,
                                     CALIBRATION_FIELD_VELOCITY, 
                                     256,
                                     print_measurements);
  if(!ok) {
    LOG_ERROR("Joint-%i: calibrating failed", joint_idx);
    return false;
  }

  servo_controller->set_enc_to_pos_lut(encoder_raw_to_motor_pos_lut);
  servo_controller->set_pos_to_field_lut(motor_pos_to_field_angle_lut);
  is_calibrated = true;
  is_homed = true;

  LOG_INFO("Joint-%i: calibrating joint successful.", joint_idx);

  return true;
}

void RobotJoint::update(float dt, float one_over_dt) {
  servo_controller->update(position, dt, one_over_dt);
}

void RobotJoint::update_target(float p, float v) {
  position = p;
  velocity = v;
}

bool RobotJoint::load_calibration() {
  std::string fn1 = calib_data_filename("enc_to_pos_lut").c_str();
  std::string fn2 = calib_data_filename("pos_to_field_lut").c_str();
  if(!LittleFS.exists(fn1.c_str()) || !LittleFS.exists(fn2.c_str())) {
    LOG_WARNING("Joint-%i: Not all calibration files found. Run joint calibration with M56.", joint_idx);
    return false;
  }

  LookupTable enc_to_pos_lut;
  LookupTable pos_to_field_lut;
  bool res = true; 
  res &= load_lut_from_file(enc_to_pos_lut, fn1.c_str());
  res &= load_lut_from_file(pos_to_field_lut, fn2.c_str());
  if(res == false)
    return false;

  servo_controller->set_enc_to_pos_lut(enc_to_pos_lut);
  servo_controller->set_pos_to_field_lut(pos_to_field_lut);

  is_calibrated = true;
  LOG_INFO("Joint-%i: Encoder lookup tables loaded (size=%i,%i)", 
           joint_idx, enc_to_pos_lut.size(), pos_to_field_lut.size());

  return true;
}

bool RobotJoint::store_calibration() {
  bool res = true;

  res &= save_lut_to_file(servo_controller->get_enc_to_pos_lut(), 
                          calib_data_filename("enc_to_pos_lut").c_str());
  res &= save_lut_to_file(servo_controller->get_pos_to_field_lut(), 
                          calib_data_filename("pos_to_field_lut").c_str());

  return res;
}

std::string RobotJoint::calib_data_filename(std::string data_name) const {
  return std::string("joint")+std::to_string(joint_idx)+"_"+data_name+".dat";
}

//--- Robot -----------------------------------------------------------------------------

Robot::Robot(float path_segment_time_step) : 
  path_planner(nullptr, path_segment_time_step), 
  motion_controller(&path_planner),
  servo_loop_frequency_counter(10000),
  motion_controller_frequency_counter(1000),
  shared_data(SPINLOCK_ID_SHARED_DATA),
  joints_spin_lock(spin_lock_instance(SPINLOCK_ID_JOINTS))
{
  kinematic_model = new KinematicModel_Delta3D();
  path_planner.set_kinematic_model(kinematic_model);

  for(int i=0; i<NUM_JOINTS; i++)
    joints[i] = nullptr;

  command_parser.set_command_processor(this);

  current_feedrate = LinearAngular(10.0f, 1.0f);
  max_acceleration = LinearAngular(500.0f, 50.0f);
  path_buffering_time_us = 50*1e3;

  state = ERobotState::IDLE;
}

Robot::~Robot() {
  if(kinematic_model != nullptr)
    delete kinematic_model;

  for(int i=0; i<NUM_JOINTS; i++) {
    if(joints[i] != nullptr)
      delete joints[i];
    joints[i] = nullptr;
  }
}
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

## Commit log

2025-09-02 motor pole pair count in config
2025-09-13 fixed critical problem in PCB layout, where a misplaced via shorted 5V rail to GND
    [ControlBoard_v1.kicad_pcb]
2025-09-17 add image of pcb drill location
2025-09-18 added STL files for printing
    [BallJointMount.stl, BaseBlock.stl, EndEffector.stl, MotorHorn.stl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]
2025-09-18 Update README.md
    Added links for STL files and V1.2 PCB repair image
2025-09-18 Update bom.txt with 3D printed parts
2025-09-18 removed old CAD part
    [WireMountFixture.FCStd]
2025-09-19 renamed stl folder
    [BallJointMount.stl, BaseBlock.stl, EndEffector.stl, MotorHorn.stl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]
2025-09-19 Version v1.0.1: * Improved homing (parallel homing support, better repeatability, better geometric reference point) * Improved joint calibration procedure * Calibration data can now be stored persist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
    New G-Code commands:
    * Enable/Disable motors command, including pose recovery from current position on motor enable
    * Dedicated joint calibration command with save to flash option
    * Set pose command to directly set a target pose for the servo loops, bypassing the motion controller (good for real-time control)
2025-10-13 added measurement print option to calibration
2025-10-18 - added raw logging - better calibration output - added calibration plotter
2025-10-20 docs: add Motor Horn to BOM
2025-10-23 feat(CAD): create RubberBand
    Add a new CAD part representing the RubberBand component.
    The model provides an approximate geometric representation of the real rubber band,
    sufficient for assembly positioning and visual reference.
    [RubberBand.FCStd]
2025-10-23 chore: update RubberBand
    [RubberBand.FCStd]
2025-10-23 feat(cad): add RubberBand and RubberBandCollet parts to main assembly and subassemblies
    Insert the RubberBand (new part) and RubberBandCollet (existing part) into the main CAD assembly and related subassemblies.
    Updated some assembly constraints and references to ensure correct placement and maintain parametric consistency.
    [Assembly_Actuator.FCStd, Assembly_MicroManipulator.FCStd, Assembly_WireFlexureUnit.FCStd]
2025-10-31 removed redundant motor mount in assembly
    [Assembly_Actuator.FCStd, Assembly_MicroManipulator.FCStd, Assembly_WireFlexureUnit.FCStd, RubberBand.FCStd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]
